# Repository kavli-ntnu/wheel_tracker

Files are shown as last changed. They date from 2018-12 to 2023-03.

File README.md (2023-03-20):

# Wheel tracker

Documentation for behavioral wheel used for head fixed in vivo recordings. It enables precise recordings of wheel movement and enforced motion via a stepper motor. The motor is coupled to the main axle via a one-way clutch. This way the animal can always outrun the (slower) motor movement, but is blocked from running backwards. Two microcontrollers are used, one for recording the wheel motion, one as stepper motor driver. This wheel is currently in use at both the femtonics as well as the miniscope setup. 

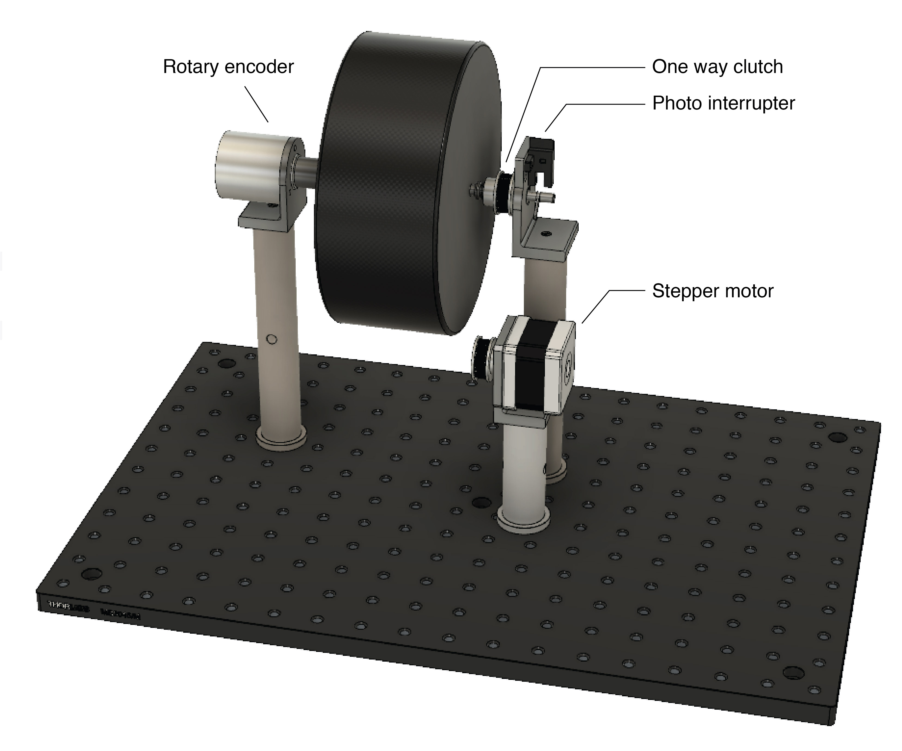
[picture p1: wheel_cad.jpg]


### Main assembly
The wheel is made from black foam and has a radius of 85mm and a width of 70mm. Larger diameters can be chosen if needed. 
- Customized aluminium parts: [STEP][step files] files | [Drawings][drawings]
- Thorlabs posts like RS2.5P/M - Ø25.0 mm Pedestal Pillar Post, M6 Taps, L = 65 mm (this is the minimum height for wheel radius 85 mm)
- Thorlabs breadboard (e.g. MB3030/M)
- One way clutch: HF0612 KULELAGER AS, Molde, NO (post@kulelager24.no)
- Bearing: HK 0608 KULELAGER AS, Molde, NO 
- Shaft coupler 6 mm inner diameter (similar to [this][shaft coupler]) to couple rotary encoder shaft and main axle of wheel
- GT2 timing belt [pulley][pulley] (this one has to be enlarged to fit bearings)
- GT2 timing [belt][belt]

### Rotary encoder and photo interrupter (microcontroller 1)
A YUMO Rotary Encoder (model E6B2-CWZ3E, see [datasheet](mouser_datasheet_YUMO.pdf)) connected to a [teensy 3.5][Teensy homepage] is used to digitize the wheel motion. A t-slot [photo interruper][t-slot] is used to record 360 degree turns. 
- Arduino [code][teensy code] teensy3.5
- [Teensy encoder library][encoder library]

Recording starts upon rising edge detection on `frameclock_pin` and stops when there was no signal on this pin for > 500 ms (adjustable, see code). This event and the detection of a beam break (photo interrupter) are detected as hardware interrupts on the teensy and sent over to the recording computer via USB serial (see section *Recorder* below) in 20 ms intervals (`interval_`). Before and after data is sent via serial the `sync pin` is switched, which can be used to record when communication happened (the delay between measurement of wheel position and initiation of data transfer is assumed to be negligible). This sync pin is connected to an event recorder (femtonics digital in or else). 
The teensy also registers user button presses (`button_pin`) and sends out a HIGH on `motor_enable_pin` to microcontroller 2 (see below) over a certain interval (`interval_motor_`). During this time a *1* will be sent over for entry *Motor* (see serial data below).

There is also arduino code for just the rotary encoder ([code][only rotary code] teensy3.5) in isolation (no motor + button interaction). 

Several versions of ´only_rotary_teensy*´ are provided for various synchronisation setups:
* only_rotary_teensy_btn : replacing the measurement input signal from an external recorder, a button attached to the arduino is used to start/stop recording manually
* only_rotary_teensy_dtr : recording happens while an active serial connection is maintained, i.e. begins automatically whenever the listening Python script is started
* only_rotary_teensy_prtc : the frame clock output pin is replaced by a pseudo-random timecode input. Whenever an input TTL is receieved, an additional output signal is sent over usb-serial declaring the timestamp (ms accuracy) at which the ttl was recieved. Can be used for post-processing alignment to the standard sync method in use for Neuropixels in the Moser group.

### Motor (microcontroller 2)
For motor control a NEMA17 stepper motor is used, controlled by [uStepper][ustepper homepage] board, running a acceleration/deceleration protocol over defined number of steps. The stepper motor driver gets triggered by the Teensy 3.5 when a button is pressed. 
- Arduino [code][ustepper code] uStepper
- [Product PDF ustepper][pdf uStepper]
- [Documentation page][documentation ustepper] for uStepper

### Serial
Data is recorded via USB connection to the teensy (see [save_tracking.py][python code wheel]). It arrives in the form `"Position_Interruped_InterruptedPosition_Motor"`, where `Position` is the integer rotary encoder position, `Interrupted` is either 0 or 1 for when a beam break was detected, `InterruptedPosition` is the integer position at the time when the beam was interrupted, `Motor` is either 0 or 1 for the times when the user pressed the button.

### Camera
For behavioral recording this setup is paired with a fast camera that tracks the animal's movements on the wheel. The camera sends a HIGH during exposure which can be logged with an event recorder as for the teensy pulses (see above).
 - Camera [acA2000-165umNIR - Basler ace][basler camera]
 - Lens [VS-1614H1N][lens]
 - GP I/O [cable][cable basler]

[logo]: wheel_cad.jpg
[shaft coupler]: https://www.geartech.no/produkter/transmission/akselkoblinger/fast-kobling/
[pulley]: https://www.adafruit.com/product/1254
[belt]: https://www.adafruit.com/product/1184

[step files]: /step_files_wheel
[drawings]: drawings_wheel.pdf

[ustepper homepage]: http://www.ustepper.com/index/
[Teensy homepage]: https://www.pjrc.com/store/teensy35.html
[t-slot]: https://www.adafruit.com/product/3985

[encoder library]: https://www.pjrc.com/teensy/td_libs_Encoder.html
[only rotary code]: /only_rotary_teensy/only_rotary_teensy.ino

[teensy code]: /motor_control_teensy/motor_control_teensy.ino

[ustepper code]: /ustepper_control_code/ustepper_control_code.ino
[documentation ustepper]: http://ustepper.com/docs/html/index.html
[pdf ustepper]: /ustepper_control_code/product_sheet_revB.pdf

[python code wheel]: save_tracking.py

[basler camera]: https://www.baslerweb.com/en/products/cameras/area-scan-cameras/ace/aca2000-165umnir/
[lens]: https://vst.co.jp/en/vs-h1-series/
[cable basler]: https://www.baslerweb.com/de/produkte/vision-komponenten/kabel/gp-i-o-cable-6p-open-10-m/

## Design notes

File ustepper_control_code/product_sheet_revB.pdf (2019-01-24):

# uStepper Rev. B

# product description

By uStepper ApS

## Microcontroller, stepper driver and encoder in an ultra-compact design!

# Features & technical specifications

uStepper is an ultra-compact Arduino compatible board, with integrated stepper driver and 12-bit rotary encoder, enabling the uStepper to be mounted directly on the back of a NEMA 17 size stepper motor. This makes it possible to develop applications using a stepper motor, without the need for long and messy wiring to an external Arduino/stepper

shield. Furthermore the 12-bit rotary encoder ensures that the absolute position of the motor shaft can be tracked, enabling the uStepper to detect any loss of steps.

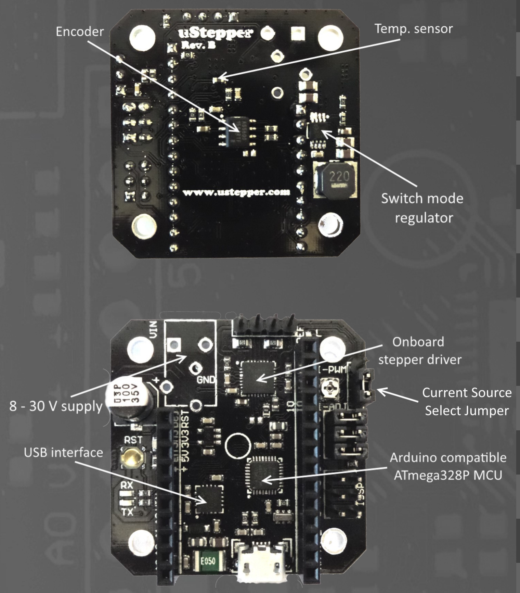
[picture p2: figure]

Microcontroller | ATmega328P (16 MHz )
I/O Voltage | 5 V
Input Voltage (recommended) | 8 - 24 V
Input Voltage (max) | 8 - 30 V
Digital I/O pins | 12 (6 of which provide PWM)
Analog I/O pins | 4
DC Current per I/O Pin (max) | 40 mA (max 200 mA total I/O draw)
DC Current for 5 V Pin (max) | 800 mA (not on USB power)
DC Current for 3.3 V Pin (max) | 50 mA
Stepper drive current | Up to 2A (adjustable)
Microstepping | Up to 16x (selectable)
Encoder resolution | 12 bit
Dimensions | 41.8 x 41.8 x 14.5 mm
Weight | ~13g

## The 5 V switch mode regulator makes it possible to supply uStepper with up to 30 V (24 V

recommended). This would be impossible with a linear regulator design.

A temperature sensor is located near the stepper driver, allowing you to continuously monitor the temperature and take action, should the temperature get too high.

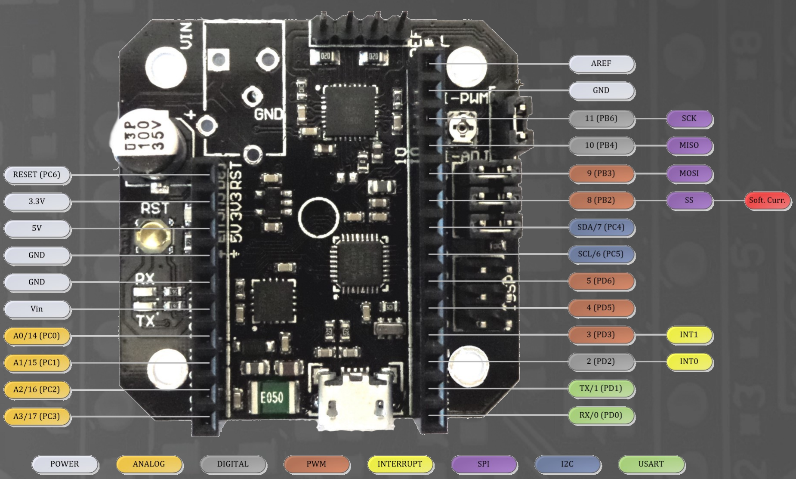
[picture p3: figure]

## As it can be seen from the PIN mapping above, uStepper offers a vast amount of GPIO’s from it’s ATmega328P MCU. This makes the uStepper capable of interacting with various sensors, actuators, communication modules etc. - Besides functioning as a stepper driver

with feedback capability.

Microstepping is selected by jumpers MS1 to MS3 (it is also possible to solder them on the back of the board for permanent microstep setting). Current limit is adjusted using the on-

## board potentiometer or using software. Current source is chosen using the Current Source

Select Jumper (see picture on the left), where lower position is chosen for the potentiometer as source.

# uStepper PIN mapping

Microstep setting | MS1 | MS2 | MS3
Full step | No | No | No
1/2 step | Yes | No | No
1/4 step | No | Yes | No
1/8 step | Yes | Yes | No
1/16 step | Yes | Yes | Yes

## Current Limit = 6.25 x Vref

## Where Vref is measured on the potentiome-

ter screw and can be between 0 and 313 mV, resulting in 0 - 2 A current limit.

# Mounting

Follow the steps below to mount uStepper on a Nema 17 size stepper motor.

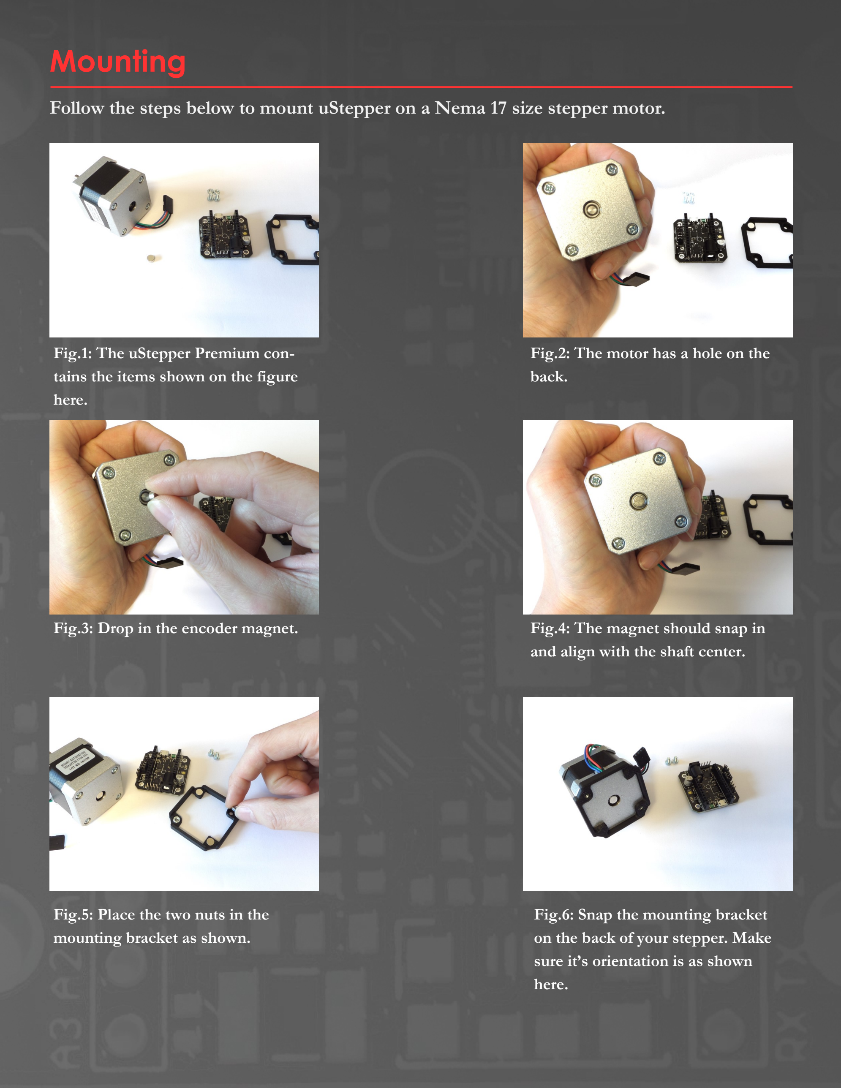
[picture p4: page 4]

### Fig.1: The uStepper Premium contains the items shown on the figure

here.

### Fig.2: The motor has a hole on the

back.

Fig.3: Drop in the encoder magnet. | Fig.4: The magnet should snap in and align with the shaft center.

### Fig.5: Place the two nuts in the

mounting bracket as shown.

### Fig.6: Snap the mounting bracket on the back of your stepper. Make sure it’s orientation is as shown

here.

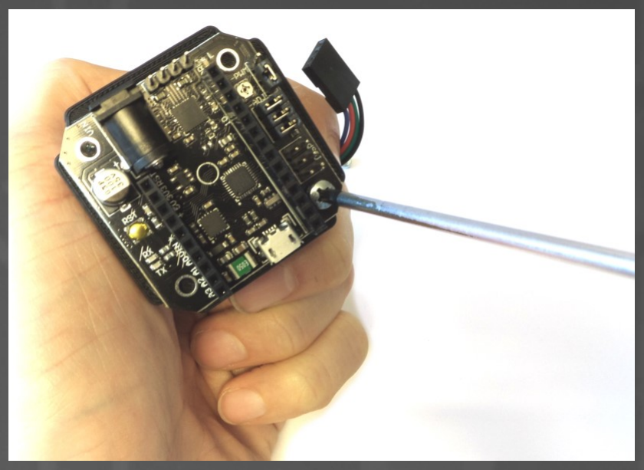
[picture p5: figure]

### Fig.7: Secure the uStepper board

with the two Philips screws.

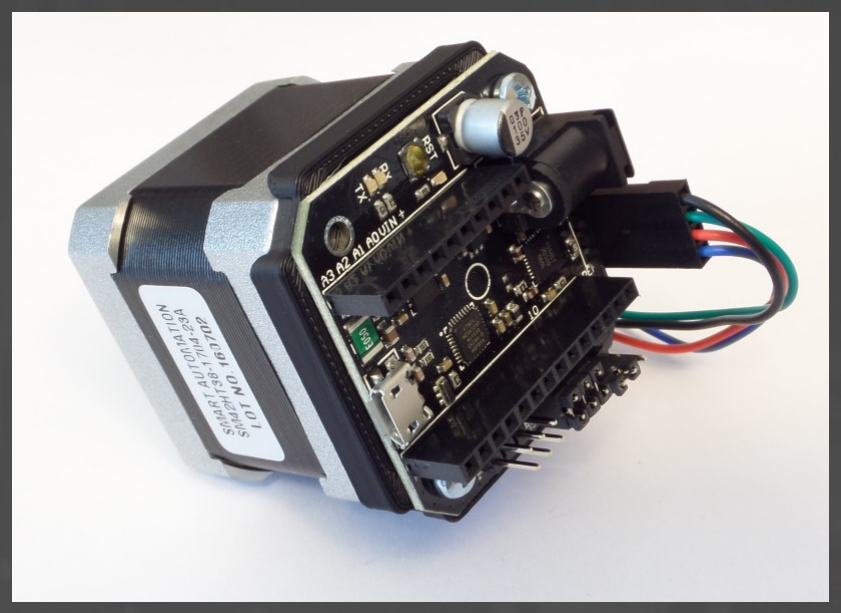
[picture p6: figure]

### Fig.8: Connect the motor, and you are done!

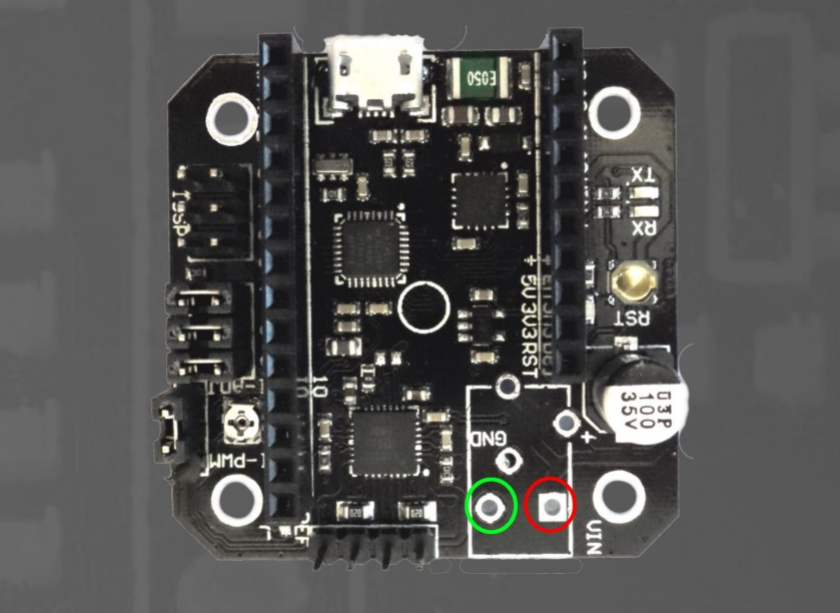
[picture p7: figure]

### Fig.9: Using screw terminals or leads. Green = GND and

Red = 8 - 24 V.

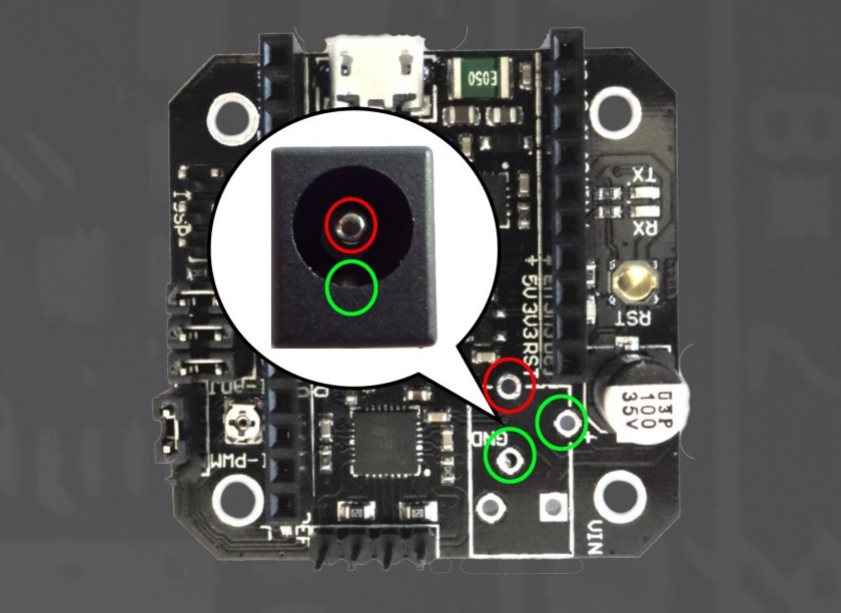
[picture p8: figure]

### Fig.10: Using DC jack. Green =

GND and Red = 8 - 24 V.

## Before turning on the power, make sure that you have connected the leads correctly and that the source provides a DC supply between 8 and

24 V.

# Applications

Because of low cost and reliability stepper motors are favored over servo drives in a variety

of applications, as for example robots, CNC machines, 3D-printers etc. With added feedback uStepper can add a new dimension to stepper operation utilizing closed loop control or correction of missed steps - making the stepper even more appealing than a more costly servo drive. With the numerous features and the vast amount of I/O’s (including various busses), uStepper is the choice for DIY hobbyists when in need of a reliable, precise and

compact actuator for almost any application.

## Almost unlimited applications and ease of programming using the Arduino IDE also

makes uStepper well suited for educational purposes.

# Application examples

# ”After all, learning just gets a bit more fun when there’s movement involved!”

Robotic arm using 3 uSteppers | Multi purpose linear actuator

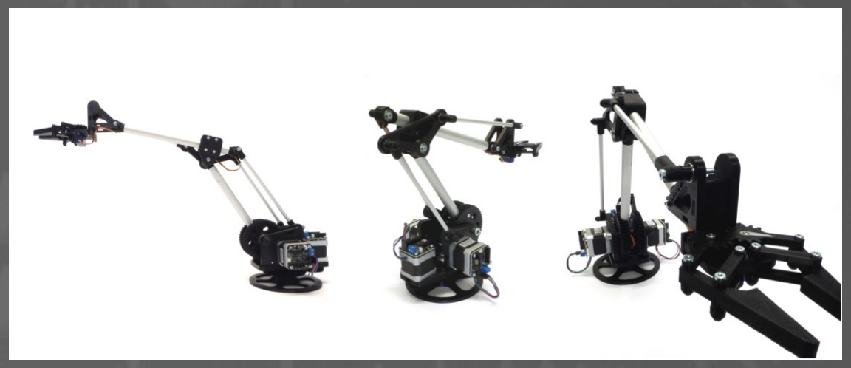
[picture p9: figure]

### The uStepper Robotic Arm is a good example of how 3 uSteppers can be put to use in an exciting and educational application. If you are eager to learn about kinematics, or just want to have your own cool robot arm at

home, this could be a good candidate.

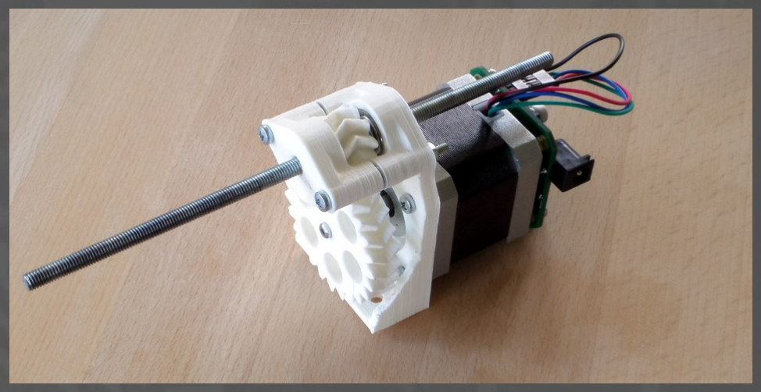
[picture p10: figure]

### The linear actuator is fitted tightly on a NEMA 17 sized stepper motor. The ultra compact uStepper fitted on the stepper gives precise control with possibility for feedback – giving the opportunity to compensate for lost steps if

needed.

# Contact

uStepper ApS
sales@ustepper.com

www.uStepper.com

# Disclaimer

1 Disclaimers and Limitation of Liability

1.1 uStepper ApS and/or ON Development IVS (or any individuals affiliated with either of the two companies) can not be held responsible for any damage inflicted upon mounting or interfacing with the uStepper board. This also includes damage to stepper motor (both electrical and mechanical) or any other 3rd party hardware connected to uStepper. Most stepper motor cases are made of aluminum, and care must be taken when preparing the mountings for uStepper.

1.2 By using the uStepper products (including, but not limited to, hardware and software) you acknowledge that uStepper ApS and/or ON Development IVS (or any individuals affiliated with either of the two companies) can not be held responsible for any personal injuries and/or damage to any 3rd party hardware that may occur when using the uStepper products.

1.3 To the extent permitted by law, uStepper ApS and/or ON Development IVS will not be liable for any indirect or consequential loss or damage, of any kind, (including without limitation loss of business, opportunity, data, profits) arising out of or in connection with the use of any products (including, but not limited to, hardware and software), developed, produced or sold by uStepper ApS and/or ON Development IVS (or any individuals affiliated with either of the two companies).

1.4 Nothing in these Terms and Conditions shall be construed so as to hold uStepper ApS and/or ON Development IVS liable for death or personal injury as a result of the negligence of uStepper ApS and/or ON Development IVS or that of its employees or agents.

2 Indemnity

2.1 You agree to indemnify and hold uStepper ApS and/or ON Development IVS and its employees and agents harmless from and against all liabilities, legal fees, damages, losses, costs and other expenses in relation to any claims or actions brought against uStepper ApS and/or ON Development IVS arising out of any breach by you of these Terms and Conditions or other liabilities arising out of your use of this Website.

2.2 You agree to indemnify and hold uStepper ApS and/or ON Development IVS and its employees and agents harmless from and against all liabilities, legal fees, damages, losses, costs and other expenses in relation to any claims or actions brought against uStepper ApS and/or ON Development IVS arising out of any breach by you of these Terms and Conditions or other liabilities arising out of your use of products(including, but not limited to, hardware and software) developed, produced or sold by uStepper ApS and/or ON Development IVS (or any individuals affiliated with either of the two companies).

3 Severance

If any of these Terms and Conditions should be determined to be invalid, illegal or unenforceable for any reason by any court of competent jurisdiction then such Term or Condition shall be severed and the remaining Terms and Conditions shall survive and remain in full force and effect and continue to be binding and enforceable.

© 2017 uStepper ApS All Rights Reserved

## Detailed description, design files and examples can be found on www.uStepper.com

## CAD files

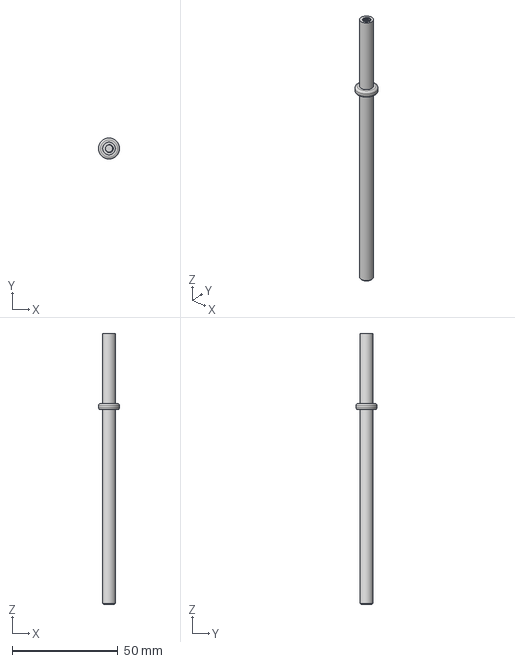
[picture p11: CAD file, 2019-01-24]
step_files_wheel/Axle Main.step
10.0 x 10.0 x 128.0 mm

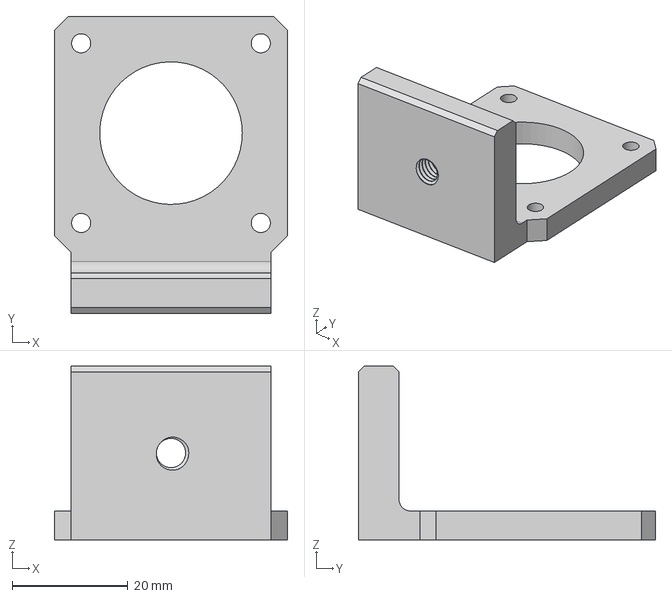
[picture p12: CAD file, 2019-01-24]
step_files_wheel/Stepper holder.step
40.3 x 51.3 x 30.0 mm

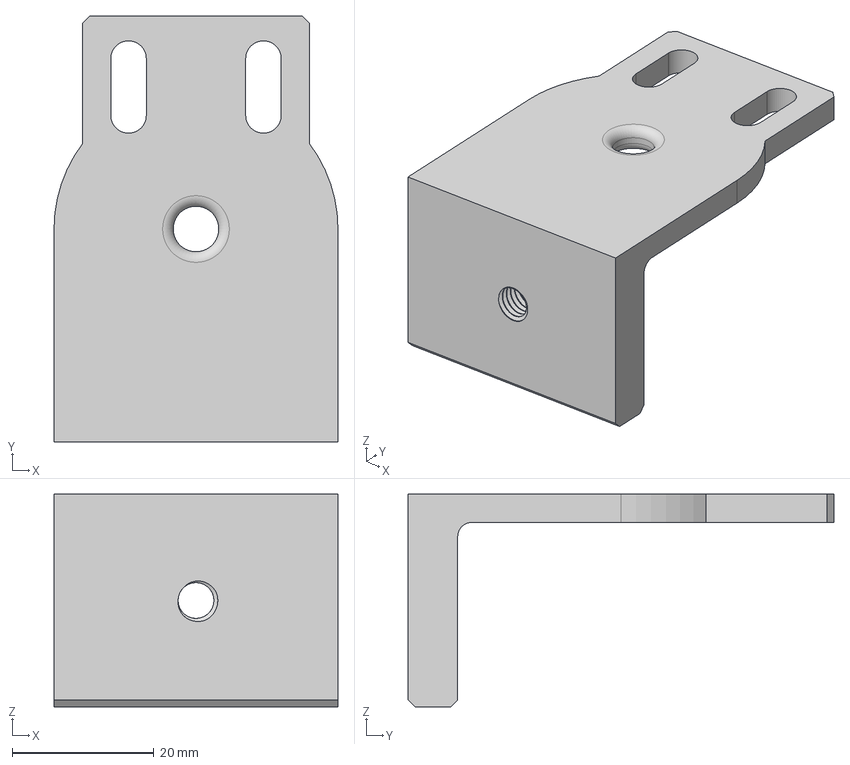
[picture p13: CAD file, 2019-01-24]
step_files_wheel/Holder 2.step
40.0 x 60.0 x 30.0 mm

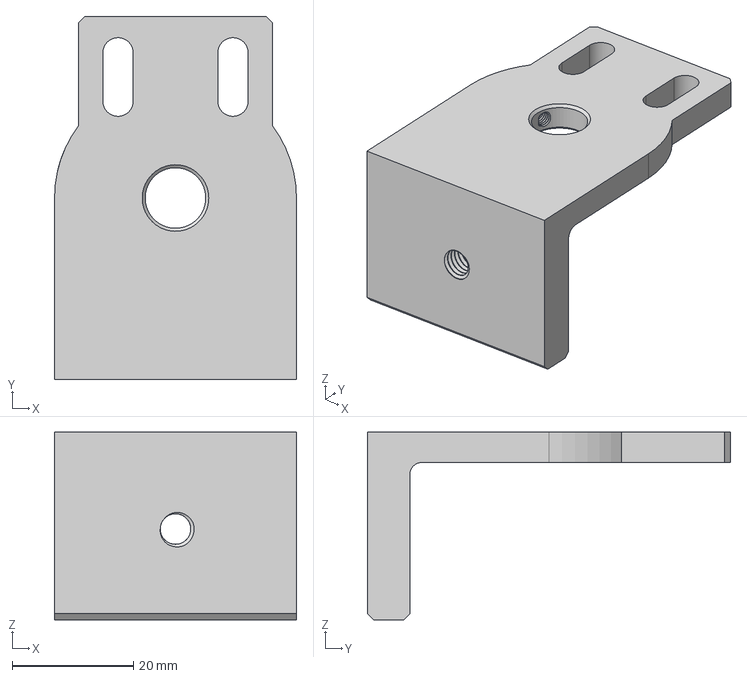
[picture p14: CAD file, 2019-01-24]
step_files_wheel/Holder 2 NEW.step
40.0 x 60.0 x 31.0 mm

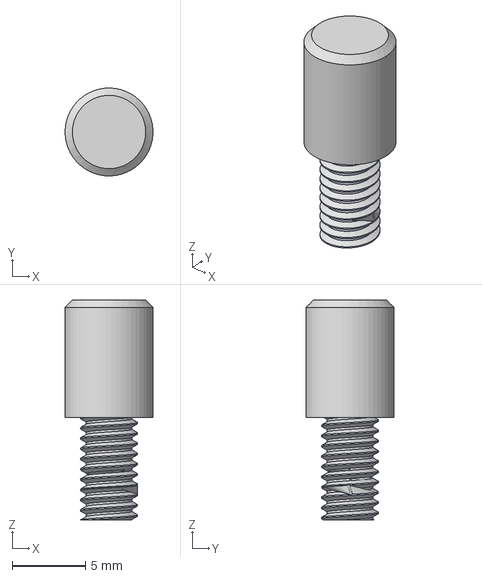
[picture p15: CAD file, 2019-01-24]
step_files_wheel/Axle end cap.step
5.99 x 6.00 x 15.0 mm

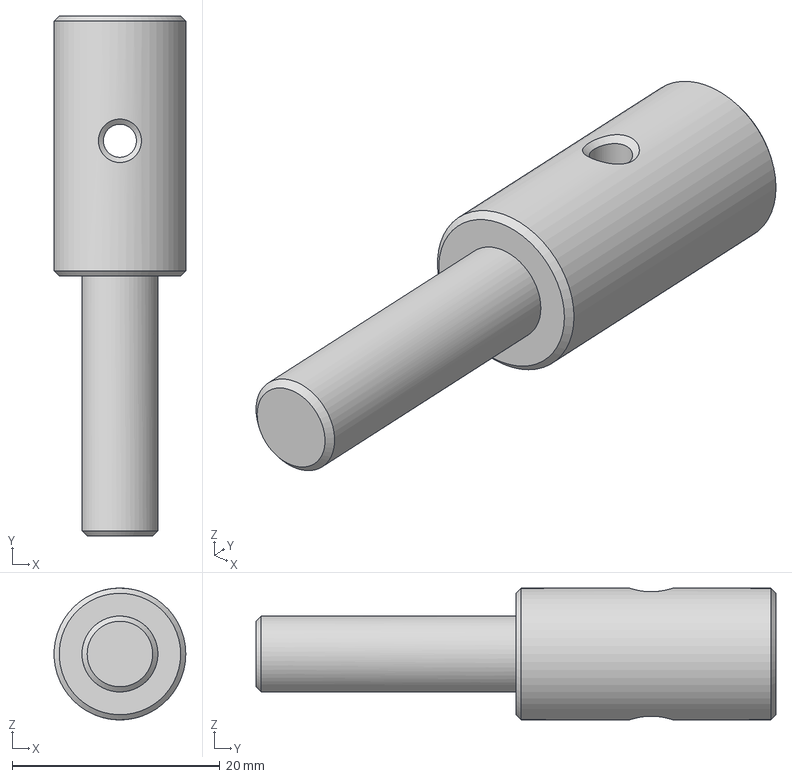
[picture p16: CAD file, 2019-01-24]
step_files_wheel/ChickenLegBar.step
12.7 x 50.0 x 12.7 mm

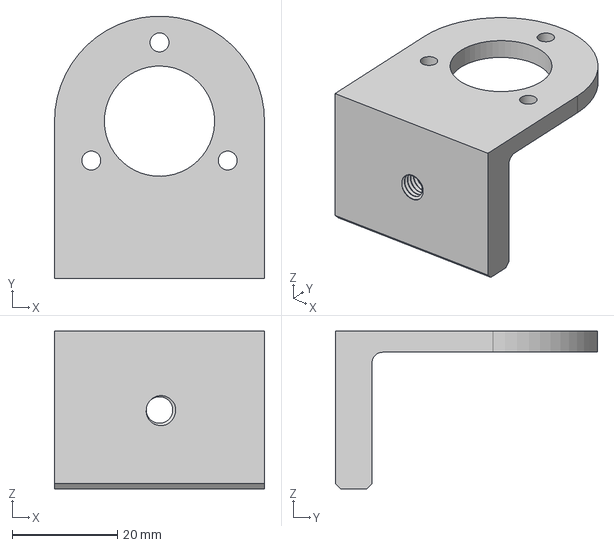
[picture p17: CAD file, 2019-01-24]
step_files_wheel/Holder 1.step
40.0 x 50.0 x 30.0 mm

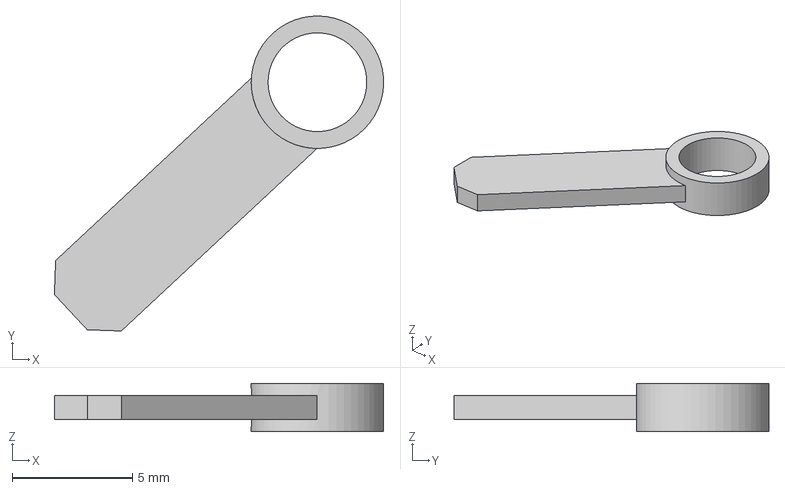
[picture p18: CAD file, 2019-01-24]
step_files_wheel/Indicator axle NEW.step
13.7 x 13.1 x 2.00 mm

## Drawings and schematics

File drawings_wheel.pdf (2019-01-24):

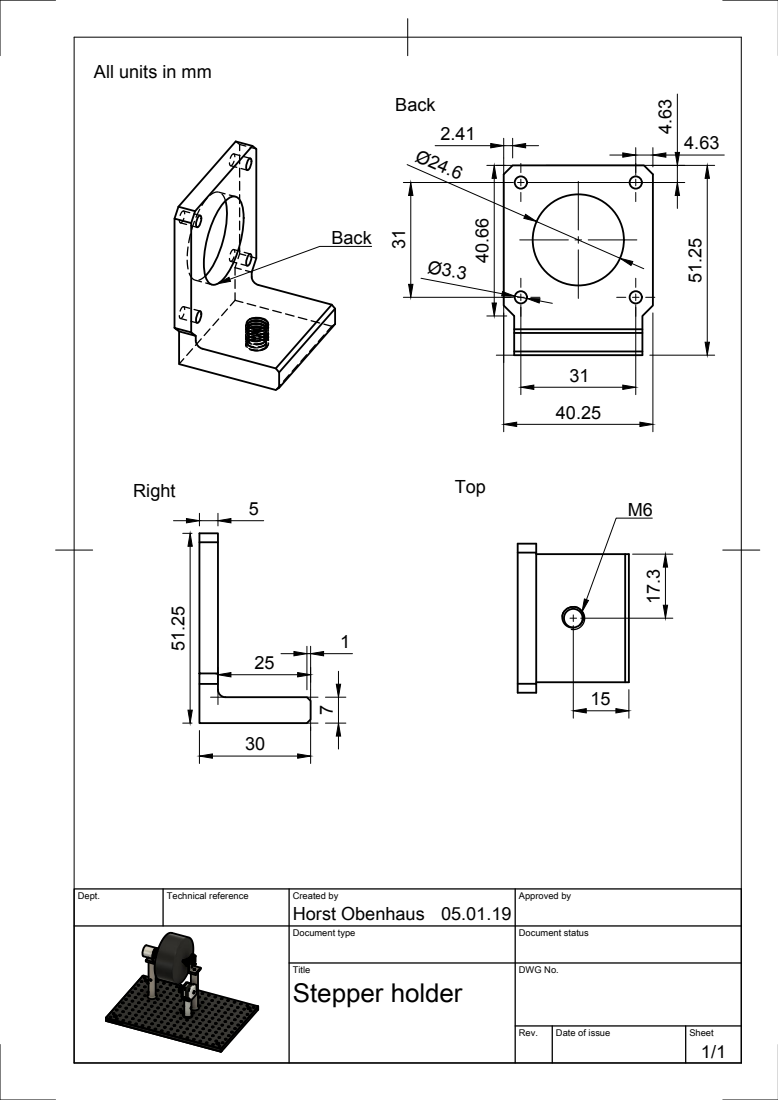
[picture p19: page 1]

All units in mm

Dept. | Technical reference | Created by Horst Obenhaus 05.01.19 | Approved by

Document type | Document status

Title Stepper holder | DWG No.

Rev. | Date of issue | Sheet

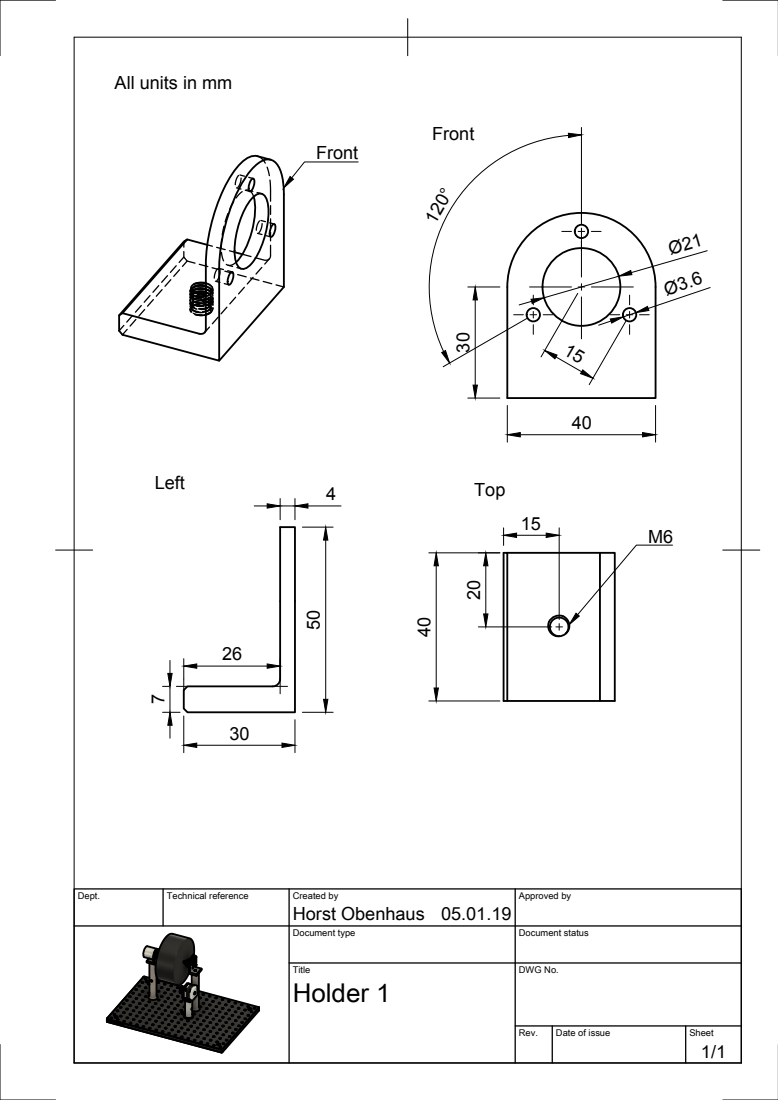
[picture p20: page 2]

Dept. | Technical reference | Created by Horst Obenhaus 05.01.19 | Approved by

Document type | Document status

Title Holder 1 | DWG No.

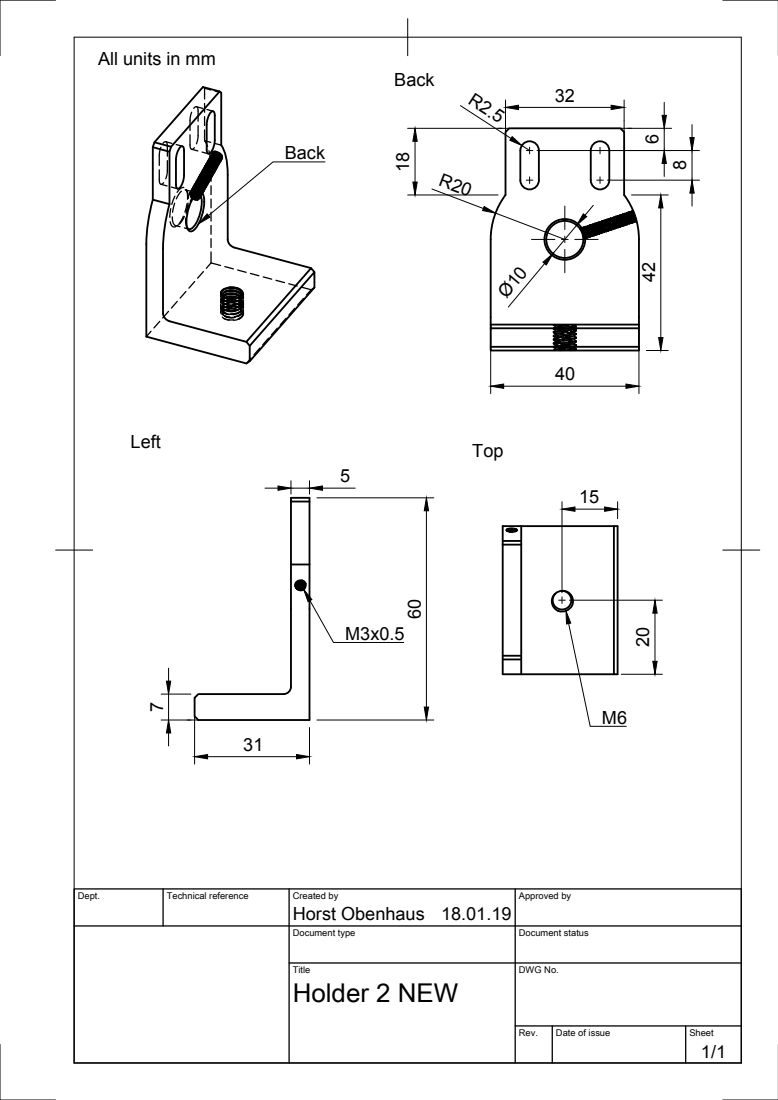
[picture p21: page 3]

Dept. | Technical reference | Created by Horst Obenhaus 18.01.19 | Approved by

Document type | Document status

Title Holder 2 NEW | DWG No.

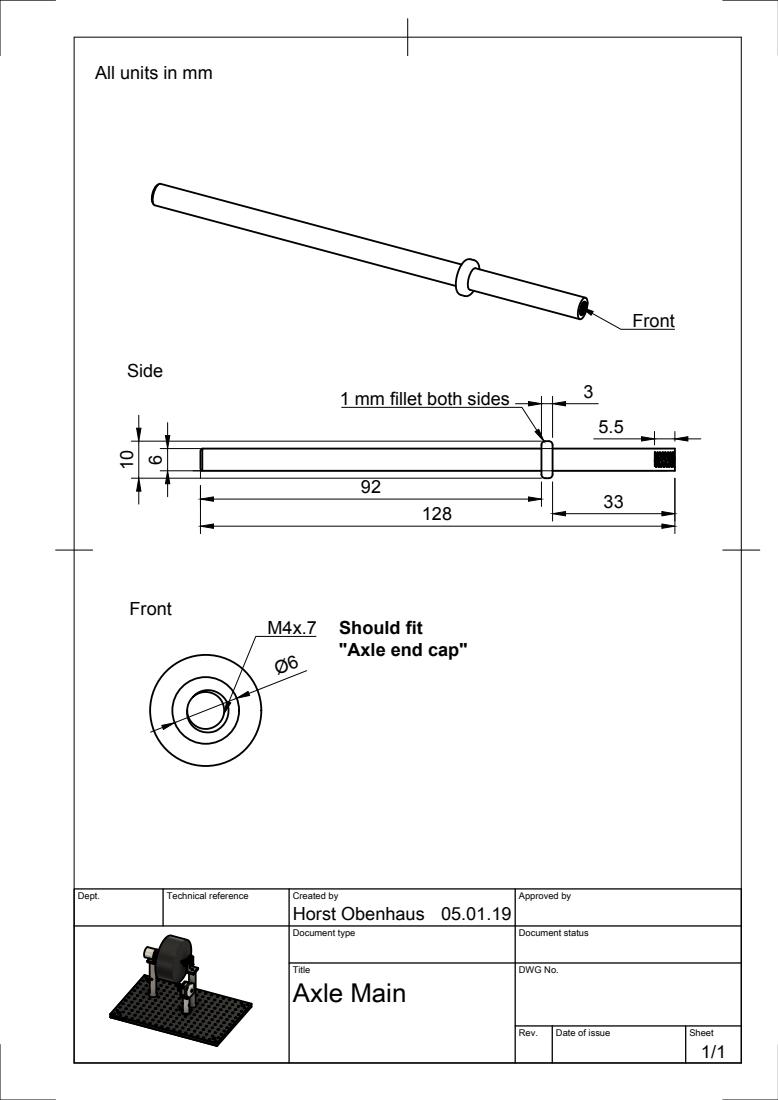
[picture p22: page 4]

1 mm fillet both sides

Should fit
"Axle end cap"

Dept. | Technical reference | Created by Horst Obenhaus 05.01.19 | Approved by

Document type | Document status

Title Axle Main | DWG No.

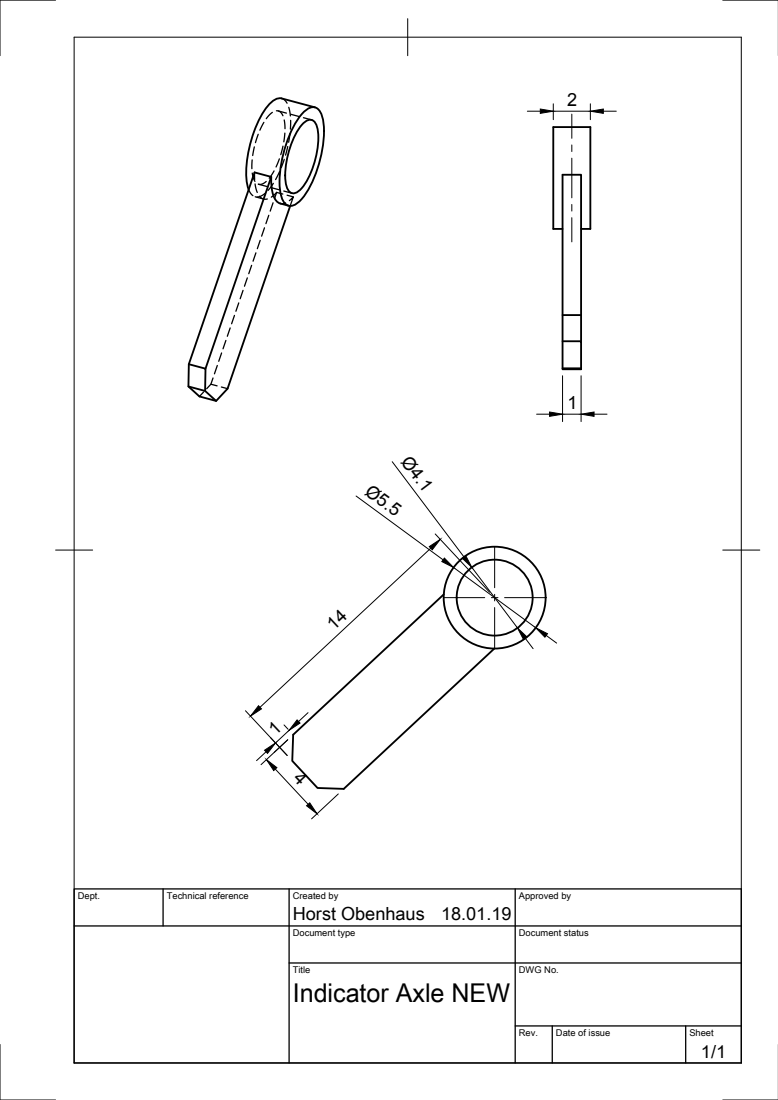
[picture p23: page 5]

Dept. | Technical reference | Created by Horst Obenhaus 18.01.19 | Approved by

Document type | Document status

Title Indicator Axle NEW | DWG No.

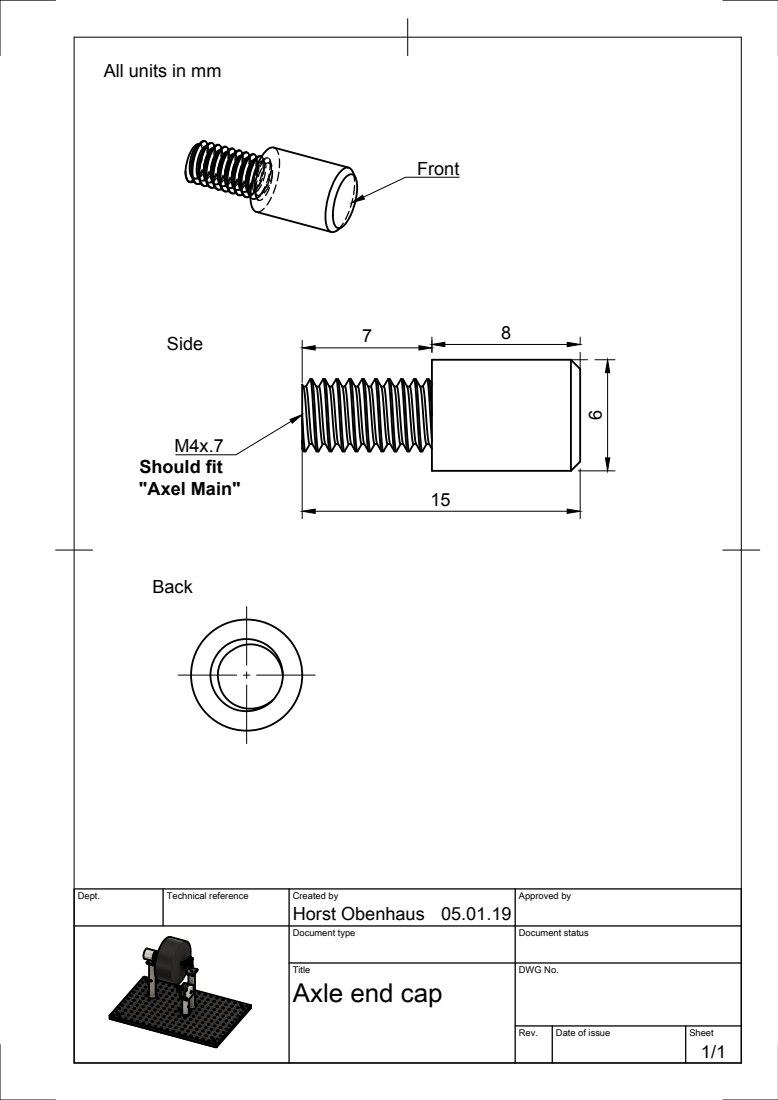
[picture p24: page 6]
Should fit "Axel Main"

Dept. | Technical reference | Created by Horst Obenhaus 05.01.19 | Approved by

Document type | Document status

Title Axle end cap | DWG No.

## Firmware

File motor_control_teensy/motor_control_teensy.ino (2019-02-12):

// Teensy 3.5 control of behavioral wheel
#include <Encoder.h>

const int motor_enable_pin = 10;
const int button_pin = 12;
const int led = 13;
const int interrupter_pin = 9;

const int frameclock_pin = 15;
const int sync_pin = 14;
const int sync_interrupter_pin = 3;

elapsedMillis measure_timer; // measure frameclock

elapsedMillis interval_timer; // for regular intervals
unsigned int interval_ = 20;  // time in ms between serial events 

elapsedMillis interval_timer_motor;  // for regular intervals
unsigned int interval_motor_ = 2000; // Keep pin on motor controler high for this long (roughly the time the motor is turning)

bool measurement = false;
bool start_clock = true;
bool motor_enable = false;
bool interrupted = false;
bool interrupt_saved = true;

long interruptedPosition;
long newPosition;

int button_state;
int interrupter_state;

Encoder myEnc(0,1);

void setup() {
 pinMode(motor_enable_pin, OUTPUT);
 pinMode(led, OUTPUT);
 pinMode(sync_pin, OUTPUT);
 pinMode(sync_interrupter_pin, OUTPUT);
 
 pinMode(button_pin, INPUT);
 pinMode(interrupter_pin, INPUT); // has pullup attached
 pinMode(frameclock_pin, INPUT_PULLDOWN); 
 attachInterrupt(frameclock_pin, clock_detected, RISING); // Microscope frame clock
 attachInterrupt(interrupter_pin, interrupt_detected, RISING); // Beam interrupter

 Serial.begin(250000);
}

void loop() {
  newPosition = myEnc.read();
  
  // MOTOR ACTION
  button_state = digitalReadFast(button_pin);
  if(button_state == HIGH){  
     motor_enable = true;
     interval_timer_motor = 0;
  } 
  if ((interval_timer_motor <= interval_motor_) && (motor_enable == true)){
    digitalWriteFast(led, HIGH); 
    digitalWriteFast(motor_enable_pin, HIGH); 
    } else {
    motor_enable = false;
    digitalWriteFast(led, LOW); 
    digitalWriteFast(motor_enable_pin, LOW);       
  }
  
  // ROTARY ENCODER
  if (measurement == true){
   
    if (start_clock == true){ // set back timer once
      interval_timer = interval_; 
      start_clock = false;
    }
    
    if (interval_timer >= interval_){
      interval_timer = interval_timer-interval_;
      digitalWriteFast(sync_pin, HIGH);
     
      // Serial print: Position_Interruped_InterruptedPosition_Motor
      Serial.print(newPosition);
      Serial.print("_");
      if (interrupted == true){
        Serial.print("1_");
        Serial.print(interruptedPosition);
        Serial.print("_");
        interrupt_saved = true;      
        interrupted = false;
      } else {
        Serial.print("0_");
        Serial.print(interruptedPosition);
        Serial.print("_");
      }
      if (motor_enable == true) {
        Serial.println("1");
      } else {
        Serial.println("0");
      }
      
      delay(5);
      
      digitalWriteFast(sync_pin, LOW);
      }
    }

  if(measure_timer > 500){
    measurement = false;
    start_clock = true;
  }
}

void clock_detected()
{
  measurement = true;
  measure_timer = 0;
}

void interrupt_detected()
{
  interrupted = true;
  if(interrupt_saved == true){
      interruptedPosition = myEnc.read(); // save current position at interrupt
      interrupt_saved = false;            // make sure only first occurence is saved
  }
}

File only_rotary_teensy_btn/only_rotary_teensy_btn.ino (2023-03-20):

// Teensy 3.5 control of behavioral wheel
// This here only includes the rotary encoder

// This is a modified version that reacts to a button connected to 
// pin 16, instead of the frame clock
// This is because the neuropixel setup can apparently not send out TTLs 
// for start / stop of measurements



#include <Encoder.h>
#include <Bounce.h>

const int led = 13;
const int button_led = 17; // That is the LED inside the pushbutton 
const int interrupter_pin = 9;

const int button_pin = 16;
const int sync_pin = 15;
Bounce push_button = Bounce(button_pin, 250);  // 250 ms debounce

elapsedMillis interval_timer; // for regular intervals
unsigned int interval_ = 20;  // time in ms between serial events 

bool measurement = false;
bool start_clock = true;
bool interrupted = false;
bool interrupt_saved = true;
bool led_state = LOW;

long interruptedPosition;
long newPosition;

Encoder myEnc(0,1);

void setup() {
 pinMode(led, OUTPUT);
 pinMode(button_led, OUTPUT);
 pinMode(sync_pin, OUTPUT);
 
 pinMode(interrupter_pin, INPUT); // either this or attach external pullup
 pinMode(button_pin, INPUT_PULLUP); 
 attachInterrupt(interrupter_pin, interrupt_detected, RISING); // Beam interrupter

 Serial.begin(500000);
}

void loop() {
  newPosition = myEnc.read();

  // Check button state
  // This starts AND stops the measurement
  if (push_button.update()) {
    if (push_button.fallingEdge()) {
        measurement = !measurement;
    }
  }

  // ROTARY ENCODER
  if (measurement == true){
    // PUSH BUTTON INTERNAL LED
    digitalWriteFast(button_led, HIGH);
    
    if (start_clock == true){ // set back timer once
      interval_timer = interval_; 
      start_clock = false;
    }
    
    if (interval_timer >= interval_){
      interval_timer -= interval_;
      digitalWriteFast(sync_pin, HIGH);
      led_state = !led_state;
      digitalWriteFast(led, led_state);
      // Serial print: Position_Interruped_InterruptedPosition_Motor
      Serial.print(newPosition);
      Serial.print("_");
      if (interrupted == true){
        Serial.print("1_");
        Serial.print(interruptedPosition);
        Serial.print("_");
        interrupt_saved = true;      
        interrupted = false;
      } else {
        Serial.print("0_");
        Serial.print(interruptedPosition);
        Serial.print("_");
      }

      Serial.println("0"); // This is reserved for motor
         
      delay(5); // Sync pin is HIGH for > 5 ms (serial print takes some time too)
      
      digitalWriteFast(sync_pin, LOW);
      }
    } else {
      digitalWriteFast(button_led, LOW);
      start_clock = true;
      digitalWriteFast(led, LOW);
    }


}


void interrupt_detected()
// A full rotation of the wheel
{
  interrupted = true;
  if(interrupt_saved == true){
      interruptedPosition = myEnc.read(); // save current position at interrupt
      interrupt_saved = false;            // make sure only first occurence is saved
  }
}

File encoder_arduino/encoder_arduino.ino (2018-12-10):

/*
 Rotary encoder code

 Sends values "newPosition" over serial.

 */
#include <Encoder.h>
elapsedMillis interval_timer; // for regular intervals
elapsedMillis measure_timer; // measure frameclock
unsigned int interval_ = 25; // time in ms between serial events

int frameclock_pin = 3;
int beambreak_pin = 17;
int sync_pin = 4; // "wheel serial"
int sync_beambreak_pin = 15;

bool measurement = false;
bool start_clock = true;
int sync_state = LOW;
int status_measure;
int status_beambreak;

Encoder myEnc(1,0);

void setup() {
  Serial.begin(250000);
  pinMode(frameclock_pin, INPUT);
  pinMode(beambreak_pin, INPUT);
  pinMode(sync_pin, OUTPUT);
  pinMode(sync_beambreak_pin, OUTPUT);
}

void loop() {
   long newPosition = myEnc.read();
   status_measure = digitalReadFast(frameclock_pin);
   status_beambreak = digitalReadFast(beambreak_pin);

   if (status_measure == HIGH){
      measurement = true;
      if (start_clock == true){
        interval_timer = interval_;
        start_clock = false;
      }
      measure_timer = 0;
   } 

  if (measurement == true){
    if (interval_timer >= interval_){
      interval_timer = interval_timer-interval_;
      digitalWrite(sync_pin, HIGH);
      if (status_beambreak == LOW){ // beam break goes low when interrupted
        digitalWrite(sync_beambreak_pin, HIGH);
      }
      Serial.println(newPosition);
      delay(5);
      digitalWrite(sync_pin, LOW);
      digitalWrite(sync_beambreak_pin, LOW);
      }
    }

  if(measure_timer > 1000){
    measurement = false;
    start_clock = true;
  }
}

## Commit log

2018-05-12 Working version of tracker
    Changed Arduino and python code.
    Synchronisation works as follows at the moment:
    Teensy 3.5 gets as input the frame clock - whenever it registers a HIGH and the timer is > specified interval (e.g. 20 ms for 50 Hz) it then writes the current rotary encoder value via serial. While 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
    Everything runs in the exact same wavesurfer protocol as before which has only been modified to record one more digital input line (the wheel HIGH / LOW during serial write).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
2018-06-12 Current arduino code for femto
2018-06-12 Updates to arduino (formatting) and tracking code femto
2018-12-10 Added beam break sensor
    Recorded on pin 17, will go low when activated and send out a signal over pin 15 (logical high) in sync with wheel logging.
2019-01-23 Update tracker code
    New motor control teensy script
2019-01-23 Change checking for frame clock to hardware interrupt
    Hardware interrupt is much more reliable and possible on Teensy 3.5.
2019-01-24 added cad files and updated README
    [Axle Main.step, Axle end cap.step, ChickenLegBar.step, Holder 1.step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]
2019-01-28 Record femtonics frameclock and elongate pulses
    Since femtonics frameclock gives pulses that are too short (end of each frame), those pulses have to be elongated. Elongating with Teensy3.5 that has a hardware interrupt attached, which switches an 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
2019-02-11 Make miniscope compatible + add only rotary script (omitting motor control)
2019-02-18 Light internal LED during measurement
2019-02-19 Again problems with Teensy. Resoldered everything and changed to "external" pullup
2019-03-11 Don't switch on onboard LED during recordings (only rotary sketch)
2023-01-13 Python and arduino (teensy) code for pushbutton
    Push of the button starts and stops measurement. Sync output through BNC for every logged signal.
2023-01-13 Make board internal LED blink in sync to sync output
2023-01-13 Get rid of unused timer
    The measure_timer was previously used to measure time that had elapsed after no more frame clock input is detected - to end measurement.
2023-01-13 Create only_rotary_teensy_dtr.ino
    Use Serial.dtr() to detect when the serial console has been opened. https://www.pjrc.com/teensy/td_serial.html
    This is a modified version that triggers serial
    writing only when the serial connection is actually established
    i.e. when the python recorder script is running
2023-01-13 PRTC Arduino and python code
    When a serial connection is detected, a measurement is started and sync pulses and position data are logged into two separate files in the same folder.
2023-01-14 Added example data and notebook to read / display PRTC output
    [20-21-09_01-13-2023.csv, 20-21-09_01-13-2023_sync.csv, 20-23-22_01-13-2023.csv, 20-23-22_01-13-2023_sync.csv]
